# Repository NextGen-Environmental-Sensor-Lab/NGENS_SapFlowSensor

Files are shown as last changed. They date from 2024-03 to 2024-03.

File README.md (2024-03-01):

# NGENS_SapFlowSensor

Kicad files for NEXTGEN SENSOR LAB version of Justin Beslity's Sap Flow Sensor. 
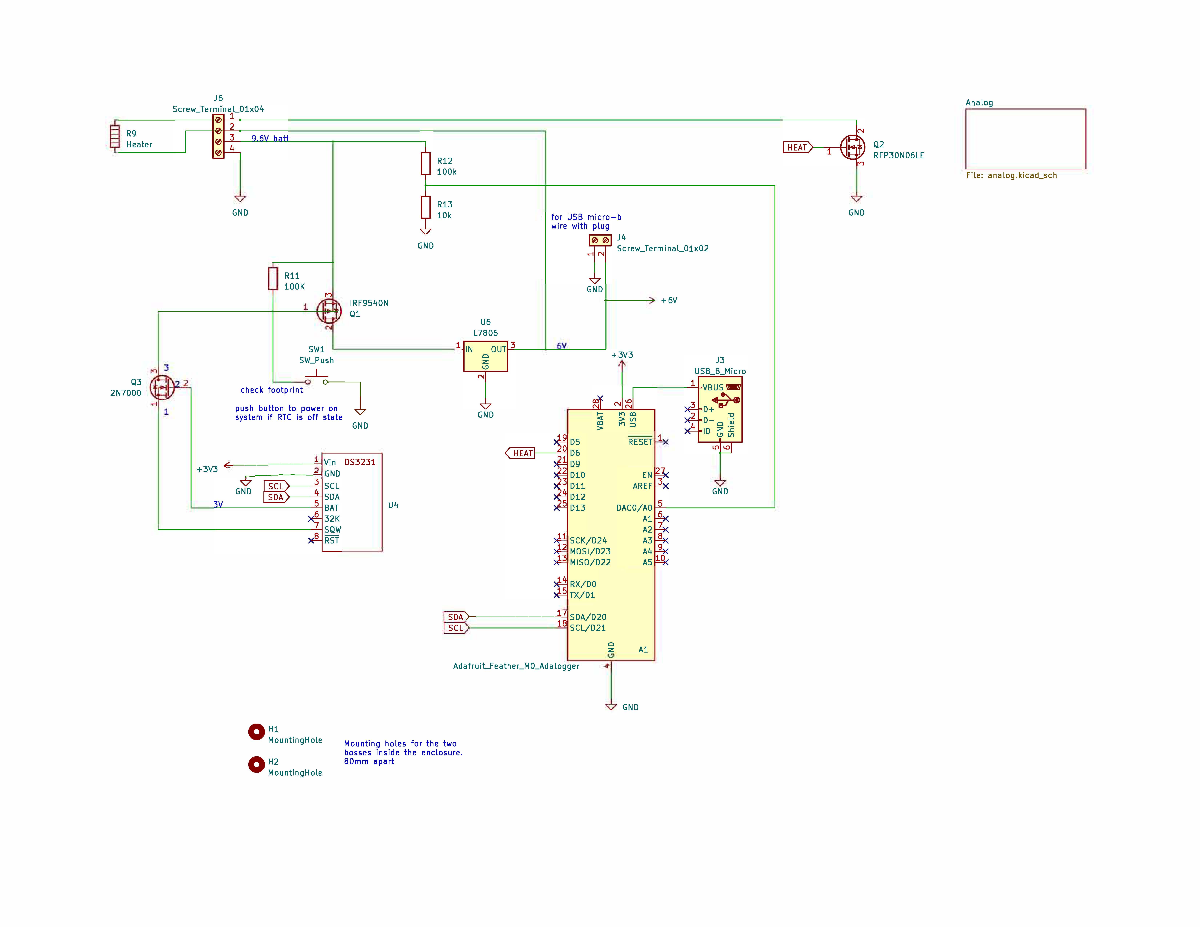
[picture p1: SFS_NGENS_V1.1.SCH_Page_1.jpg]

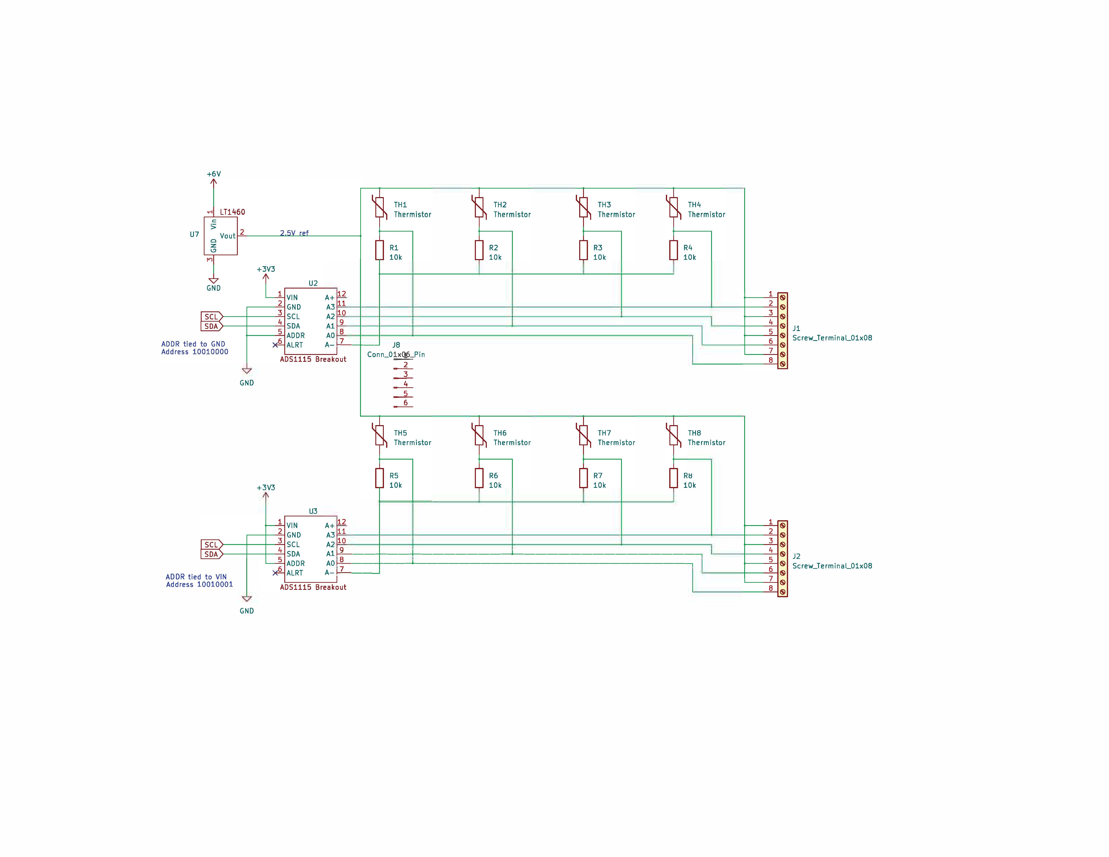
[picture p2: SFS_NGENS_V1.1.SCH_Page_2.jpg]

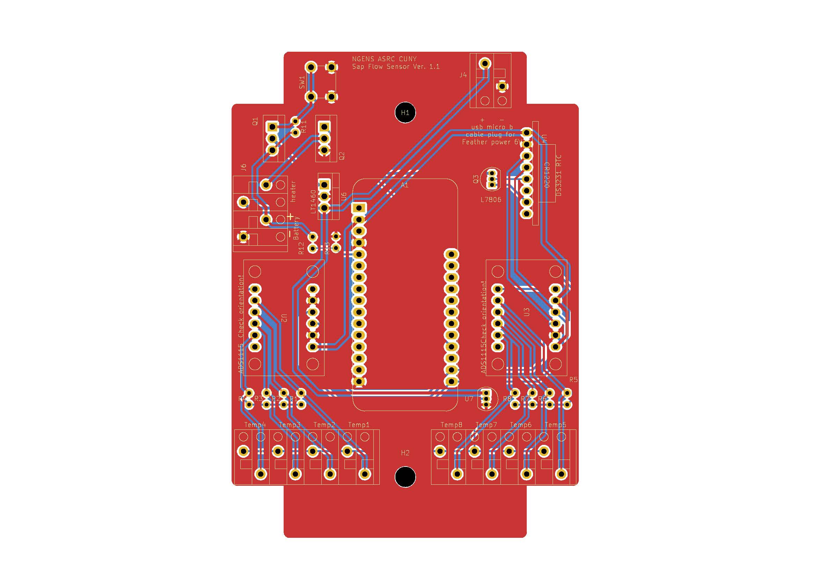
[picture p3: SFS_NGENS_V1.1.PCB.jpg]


Kicad download https://www.kicad.org/download/
Start with file SFS_NGENS_V1.1.kicad_pro

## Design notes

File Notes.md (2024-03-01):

## 2023-04-07

Starting from scratch, in KiCad.

Microcontroller: CubeCell Dev-Board Plus
    https://resource.heltec.cn/download/Manual%20Old/AB02%20User%20Maunal.pdf
    Can run on 6V input

ADC
    https://www.adafruit.com/product/1085
    We should use the A+ and A- (AVDD and AGND) pins for the thermistors. Cleaned up versions of VCC and GND, ferrites and caps.
    Address pin can be connected to GND, VDD, SDA, or SCL for 4 addresses. We'll just use GND and VDD.

Using a right-angle header for the SD card reader, so it's easier to get the card out (and to save space)
    Same for RTC
    Don't forget to add right-angle header to the BOM!

For connecting the probes, screw terminals would be better
    https://www.digikey.com/en/products/detail/w%C3%BCrth-elektronik/691210910008/11478428

## 2023-04-09

Is it ok to pull the I2C lines up to 3.3V for the ADS1115?

Is it ok to pull the SQW/INT line on the DS3231 up to battery voltage? I would think not.

How is the PMOS power shutoff supposed to work? Seems backwards.

BOM additions
    Right-angle headers
    Screw terminals
        8 and 2
    Mounting hardware for TO-220s
    Mounting screws for the PCB to the enclosure

May want to make the PCB bigger and add screw holes to mount it inside the enclosure.

## 2023-04-10

Adapting the PCB to mount inside the case
    https://www.polycase.com/wh-02
    The drawing doesn't show the dimensions of the inside of the case... bummer
    The description says "2 PCB mounting bosses in base". So maybe the 4 things in the corners are for the external mounting, and the 2 centered things are for mounting the PCB.
    They look to be 8cm apart.
    Better use slots so there's some wiggle room.

Mounting screws
    The screws specified for mounting the PCB are different from the ones that come with it for mounting the box.
        M4 x 8mm
        The ones for outside are also M4, but thread cutting
    https://www.polycase.com/screws-007-50

BOM additions
    2   https://www.digikey.com/en/products/detail/te-connectivity-amp-connectors/282834-2/1150135
    2   https://www.digikey.com/en/products/detail/te-connectivity-amp-connectors/282834-8/1150136
    1   https://www.digikey.com/en/products/detail/sullins-connector-solutions/PRPC040SBAN-M71RC/2775294
        Or similar, everyone carries this
    2   https://www.polycase.com/screws-007-50
        Screws for mounting the PCB to the enclosure. The screws that come with are different, but might work.
    Hardware for mounting the TO-220 packages, totally optional

For PFET shutoff (as in the paper), solder Q1 and R11, omit R15.
For wake-on-INT, solder R15, omit Q1 and R11, jump pins 2 and 3 of Q1.

Comments
    Flip uC around so we can access the USB port
    Use 150mil screw terminals
        Can I find one with an angle, so they can be installed while it's in the box?
        https://www.mouser.com/ProductDetail/Wurth-Elektronik/691412320008?qs=lBTPRtX1sU%2FiaSubLXxkUg%3D%3D
        https://www.mouser.com/ProductDetail/Wurth-Elektronik/691412320002?qs=lBTPRtX1sU8RrNs89OcR%252BA%3D%3D

Ok, for real, BOM additions
2   https://www.mouser.com/ProductDetail/Wurth-Elektronik/691412320008?qs=lBTPRtX1sU%2FiaSubLXxkUg%3D%3D
1   https://www.mouser.com/ProductDetail/Wurth-Elektronik/691412320004?qs=lBTPRtX1sU9B2%2FymCxYonQ%3D%3D
1   https://www.digikey.com/en/products/detail/sullins-connector-solutions/PRPC040SBAN-M71RC/2775294 or anything like it from any seller
1   https://www.polycase.com/screws-007-50

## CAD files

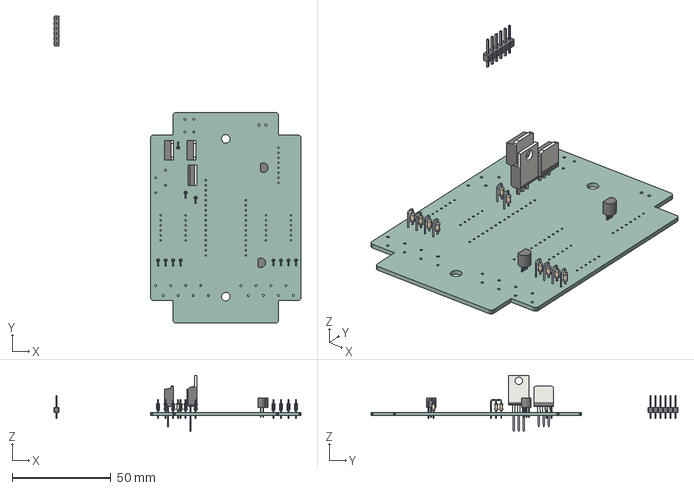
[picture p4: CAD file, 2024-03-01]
SFS_NGENS_V1.1.step
125.2 x 155.7 x 28.5 mm
Untitled PCB

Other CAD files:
PinHeader_1x06_P2.54mm_Vertical.iam
R_Axial_DIN0204_L3.6mm_D1.6mm_P2.54mm_Vertical.iam
SOLID.ipt
SOLID_1.ipt
SOLID_2.ipt
SOLID_3.ipt
SOLID_4.ipt
TO-220-3_Vertical.iam
TO-262-3_Vertical.iam
TO-92_Inline.iam
Untitled PCB.ipt
sapflowsensorpcb.iam

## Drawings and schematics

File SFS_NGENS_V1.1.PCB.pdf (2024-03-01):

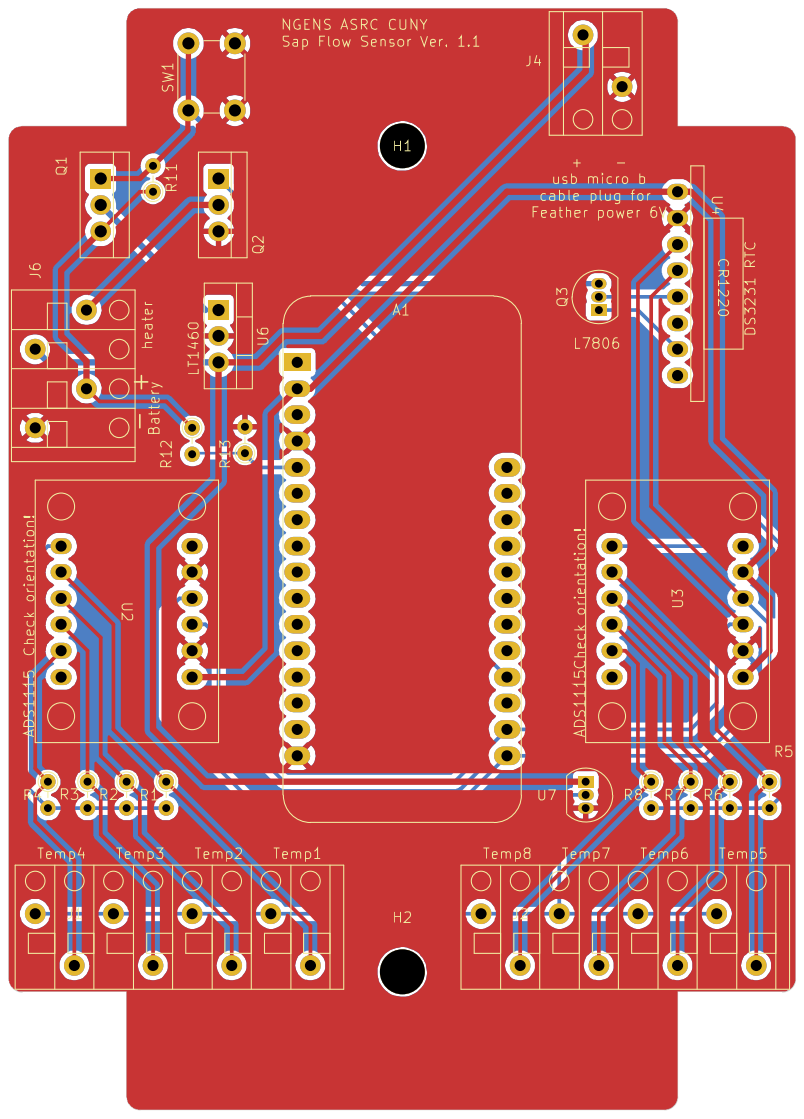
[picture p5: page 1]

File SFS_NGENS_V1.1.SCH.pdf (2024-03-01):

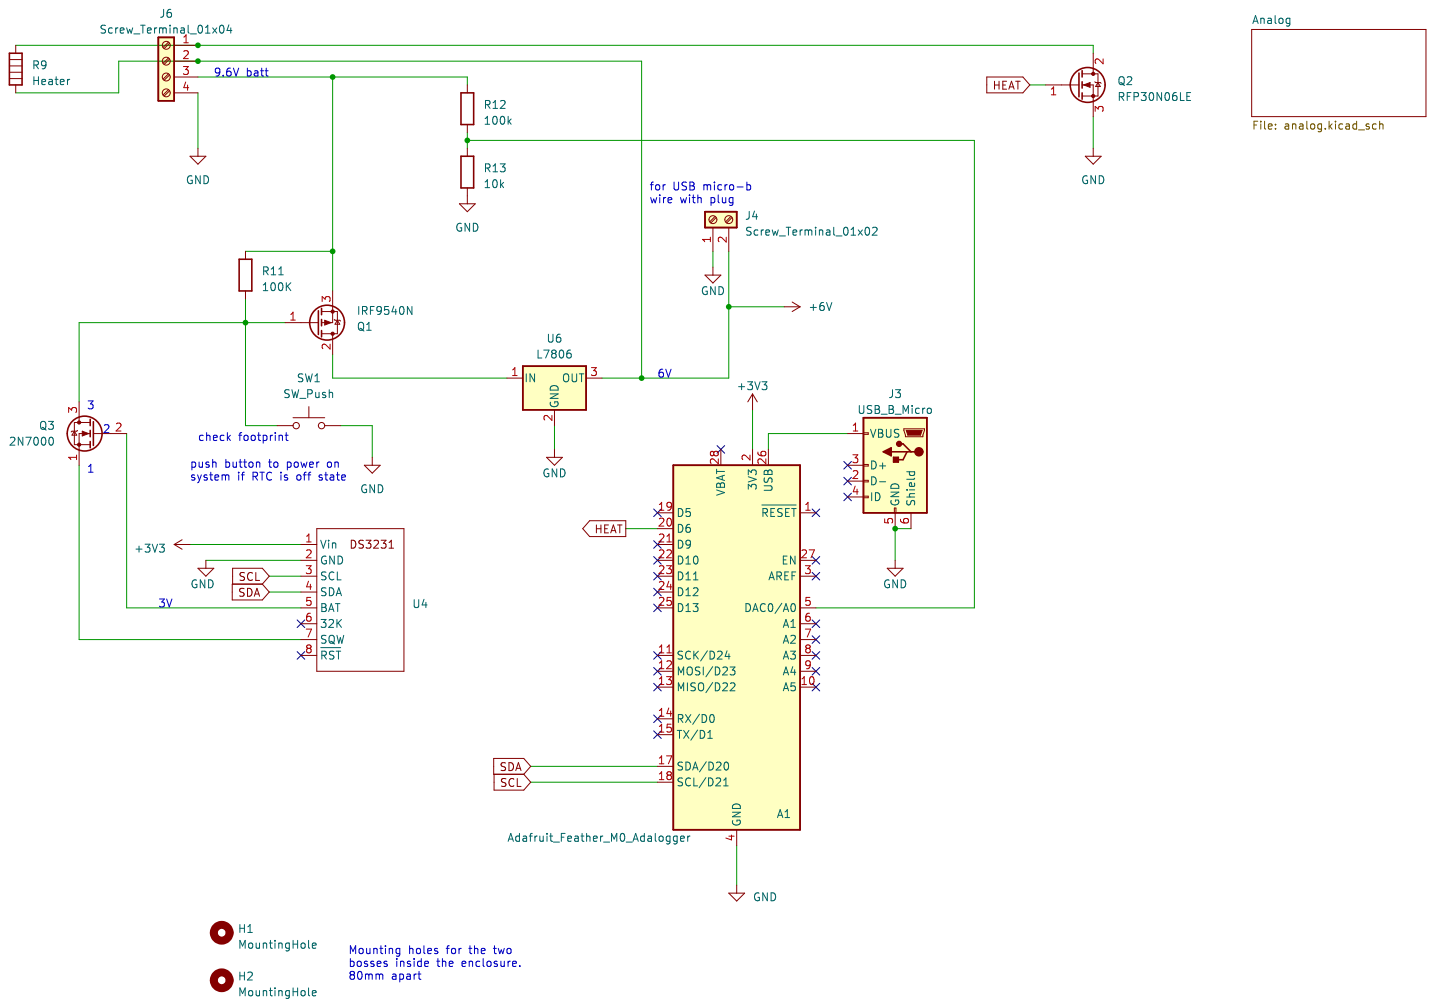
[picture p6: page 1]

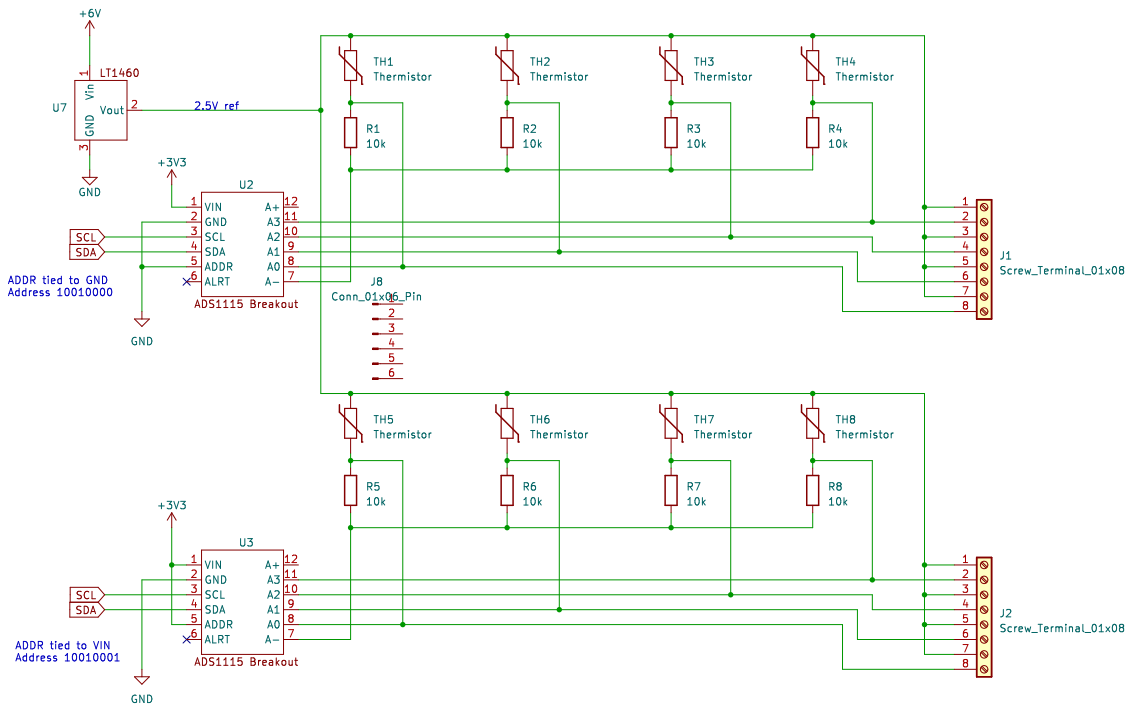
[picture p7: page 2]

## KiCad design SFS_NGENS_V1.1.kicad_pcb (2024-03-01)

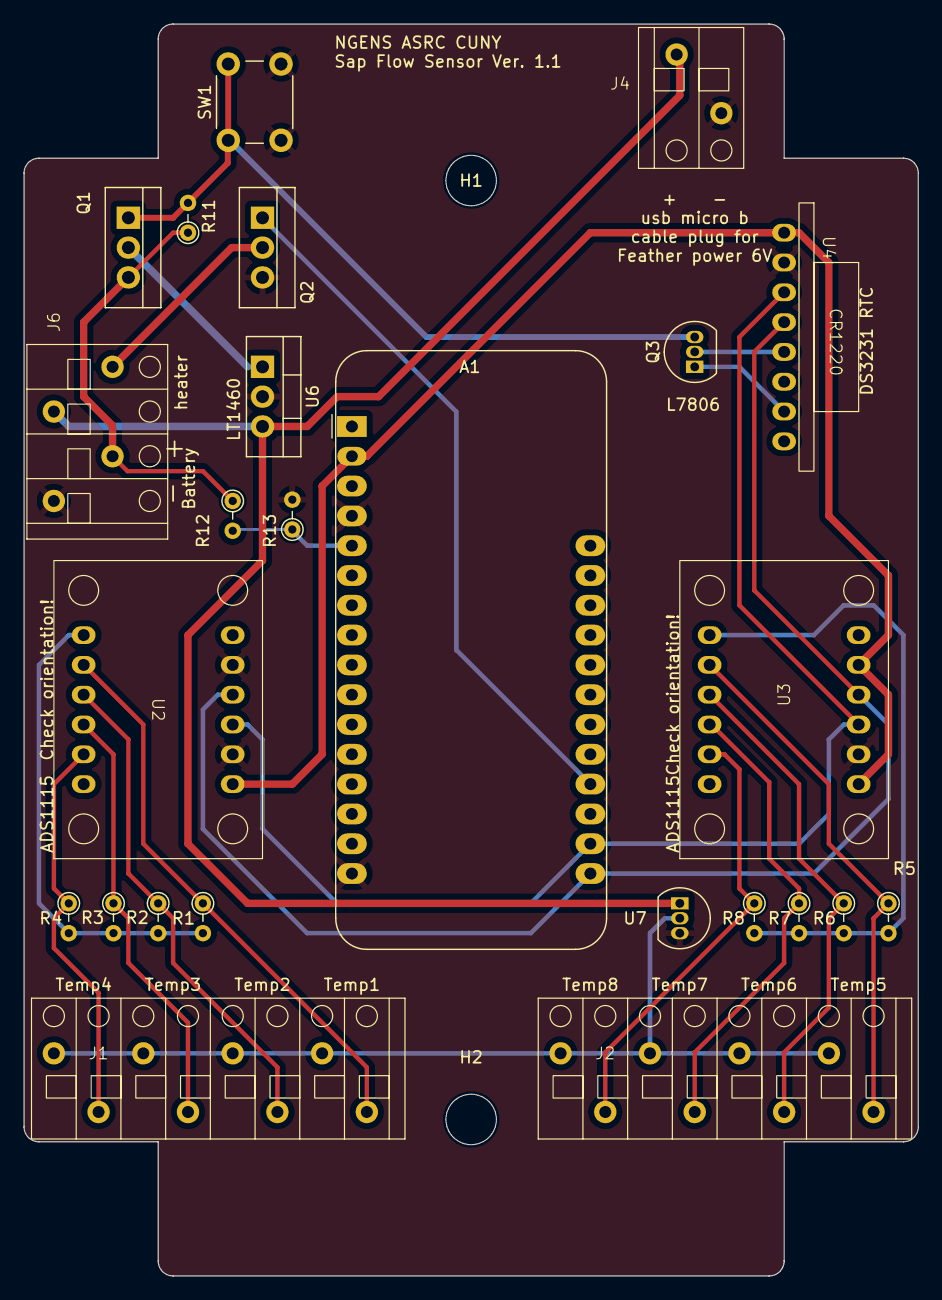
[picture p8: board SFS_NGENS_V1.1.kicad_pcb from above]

Board: 2 copper layers, 76.2 x 106.7 mm, 27 parts (0 on the bottom side), 24 nets.

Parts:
A1: Adafruit_Feather_M0_Adalogger; Adafruit_Feather
H1, H2: MountingHole; MountingHole_4.3mm_M4
J1, J2: Screw_Terminal_01x08; Wurth_Screwless45_3.81mm_8
J4: Screw_Terminal_01x02; Wurth_Screwless45_3.81mm_2
J6: Screw_Terminal_01x04; Wurth_Screwless45_3.81mm_4
Q1: IRF9540N; TO-262-3_Vertical
Q2: RFP30N06LE; TO-262-3_Vertical
Q3: 2N7000; TO-92_Inline
R1, R2, R3, R4, R5, R6, R7, R8, R13: 10k; R_Axial_DIN0204_L3.6mm_D1.6mm_P2.54mm_Vertical
R11: 100K; R_Axial_DIN0204_L3.6mm_D1.6mm_P2.54mm_Vertical
R12: 100k; R_Axial_DIN0204_L3.6mm_D1.6mm_P2.54mm_Vertical
SW1: SW_Push; SW_PUSH_6mm_H4.3mm
U2, U3: ADS1115_Breakout
U4: DS3231_Breakout_RightAngle
U6: L7806; TO-220-3_Vertical
U7: TO-92_Inline

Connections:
+3V3: A1.2 (3V3), U2.1 (VIN), U3.1 (VIN), U3.5 (ADDR), U4.1 (Vin)
+6V: J4.2, J6.2, U6.3 (OUT), U7.1 (Vin)
GND: A1.4 (GND), A1.16 (GND), J4.1, J6.4, Q2.3 (S), R13.2, SW1.2, U2.2 (GND), U2.5 (ADDR), U3.2 (GND), U4.2 (GND), U6.2 (GND), U7.3 (GND)
HEAT: A1.20 (D6), Q2.1 (G)
unnamed: A1.5 (DAC0/A0), R12.2, R13.1
unnamed: J1.1, J1.3, J1.5, J1.7, J2.1, J2.3, J2.5, J2.7, U7.2 (Vout)
unnamed: J1.2, R4.1, U2.11 (A3)
unnamed: J1.4, R3.1, U2.10 (A2)
unnamed: J1.6, R2.1, U2.9 (A1)
unnamed: J1.8, R1.1, U2.8 (A0)
unnamed: J2.2, R8.1, U3.11 (A3)
unnamed: J2.4, R7.1, U3.10 (A2)
unnamed: J2.6, R6.1, U3.9 (A1)
unnamed: J2.8, R5.1, U3.8 (A0)
unnamed: J6.1, Q2.2 (D)
unnamed: J6.3, Q1.3 (S), R11.1, R12.1
unnamed: Q1.2 (D), U6.1 (IN)
unnamed: Q1.1 (G), Q3.3 (D), R11.2, SW1.1
unnamed: Q3.2 (G), U4.5 (BAT)
unnamed: Q3.1 (S), U4.7 (SQW)
unnamed: R1.2, R2.2, R3.2, R4.2, U2.7 (A-)
unnamed: R5.2, R6.2, R7.2, R8.2, U3.7 (A-)
SCL: A1.18 (SCL/D21), U2.3 (SCL), U3.3 (SCL), U4.3 (SCL)
SDA: A1.17 (SDA/D20), U2.4 (SDA), U3.4 (SDA), U4.4 (SDA)
